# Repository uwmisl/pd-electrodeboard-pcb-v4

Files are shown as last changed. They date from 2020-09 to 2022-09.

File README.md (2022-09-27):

# Electrode Board v4

KiCad design for PurpleDrop electrode board with improved heater conductance, designed for 100x74mm film carrier and 50x50mm top plate.

This project is designed with KiCad v5.1.5.

## PDF Documentation

For a quick look, there is a [Schematic](PD_ElectrodeBoard_v4/outputs/PD_ElectrodeBoard_v4.1_sch.pdf) and [PCB fab drawing](PD_ElectrodeBoard_v4/outputs/PD_ElectrodeBoard_v4.1_fab.pdf)

## Project structure

Much of the board design is auto-generated by python scripts.

`FootprintGenerator.ipynb` generates the electrode and reservoir footprints.
They are all designed such that their origin should fall on the center of the
electrode "grid" positions. For this design, the pitch of the electrodes is
2.25mm. This script will generate a number of footprints, e.g. `electrode_points_1_40deg_rl.kicad_mod`.
The naming convention says that this footprint has 1 point per edge, the angle
of the points is 40 degrees, and it has points on the right and left edge (the
top and bottom are flat).

`FiducialFootprintGenerator.ipynb` generates a silkscreen footprint from an image file
(see `TagImages` directory), to put [april tags](https://github.com/AprilRobotics/apriltag)
onto the board as fidicuals for image processing. Each tag has a unique ID to aid in
identifying which tag (as well as which version of electrode board) has been
detected.

`LayoutGenerator.ipynb` generates a layout.yaml file for this
[kicad component layout plugin](https://github.com/mcbridejc/kicad_component_layout/).
This positions the electrodes, and selects between the different edge variants (e.g. trbl, tr)
based on neighboring electrodes in the grid.

This makes the process of experimenting with different electrode footprints and
layouts easier. Once the electrodes are positioned, the routing to the connectors
is done manually.

## BOM

| Part Number | Mfg | RefDes | Description | Qty |
| ----------- | --- | ------ | ----------- | --- |
| CLP-132-02-F-D-A  | Samtec | J1,J2  | 64-pin connectors      | 2   |
| 4929 | Keystone | H1-4 | #2-56 solderable threaded insert | 4 |
| PWR163S-25-25R0FE | Bourns | R1-4 | 25W resistor for heating | 4 |
| ZNI1000TA | Diodes Inc. | T1-4 | 1kohm RTD temperature sensor | 4 |
| S5B-PH-SM4-TB | JST | J3 | 5-pin connector for heaters | 1 |
| S8B-PH-SM4-TB | JST | J4 | 8-pin connector for RTDs | 1 |

## Revision History

### Version 4.1

- Shrinks width to fit reservoirs entirely under 50mmx50mm plate
- Corrects heater footprints
- Adds 2 internal layers to allow heaters to be located closer to the electrodes and
to provide additional thermal paths between them
- Flips connector pin labeling to match purpledrop
- 0.062" thick: 0.032" was not rigid enough
- Increases size of fiducials to 6mm and uses a unique value for each fiducial

### Version 4.0

Initial version

Issues:
- Undersized heating resistor footprints
- Mislabeled pin numbers (they do not match the purpledrop numbering)
- Fiducials were a bit too small; they silk screen resolution did not reproduce them well and sometimes they are difficult to detect

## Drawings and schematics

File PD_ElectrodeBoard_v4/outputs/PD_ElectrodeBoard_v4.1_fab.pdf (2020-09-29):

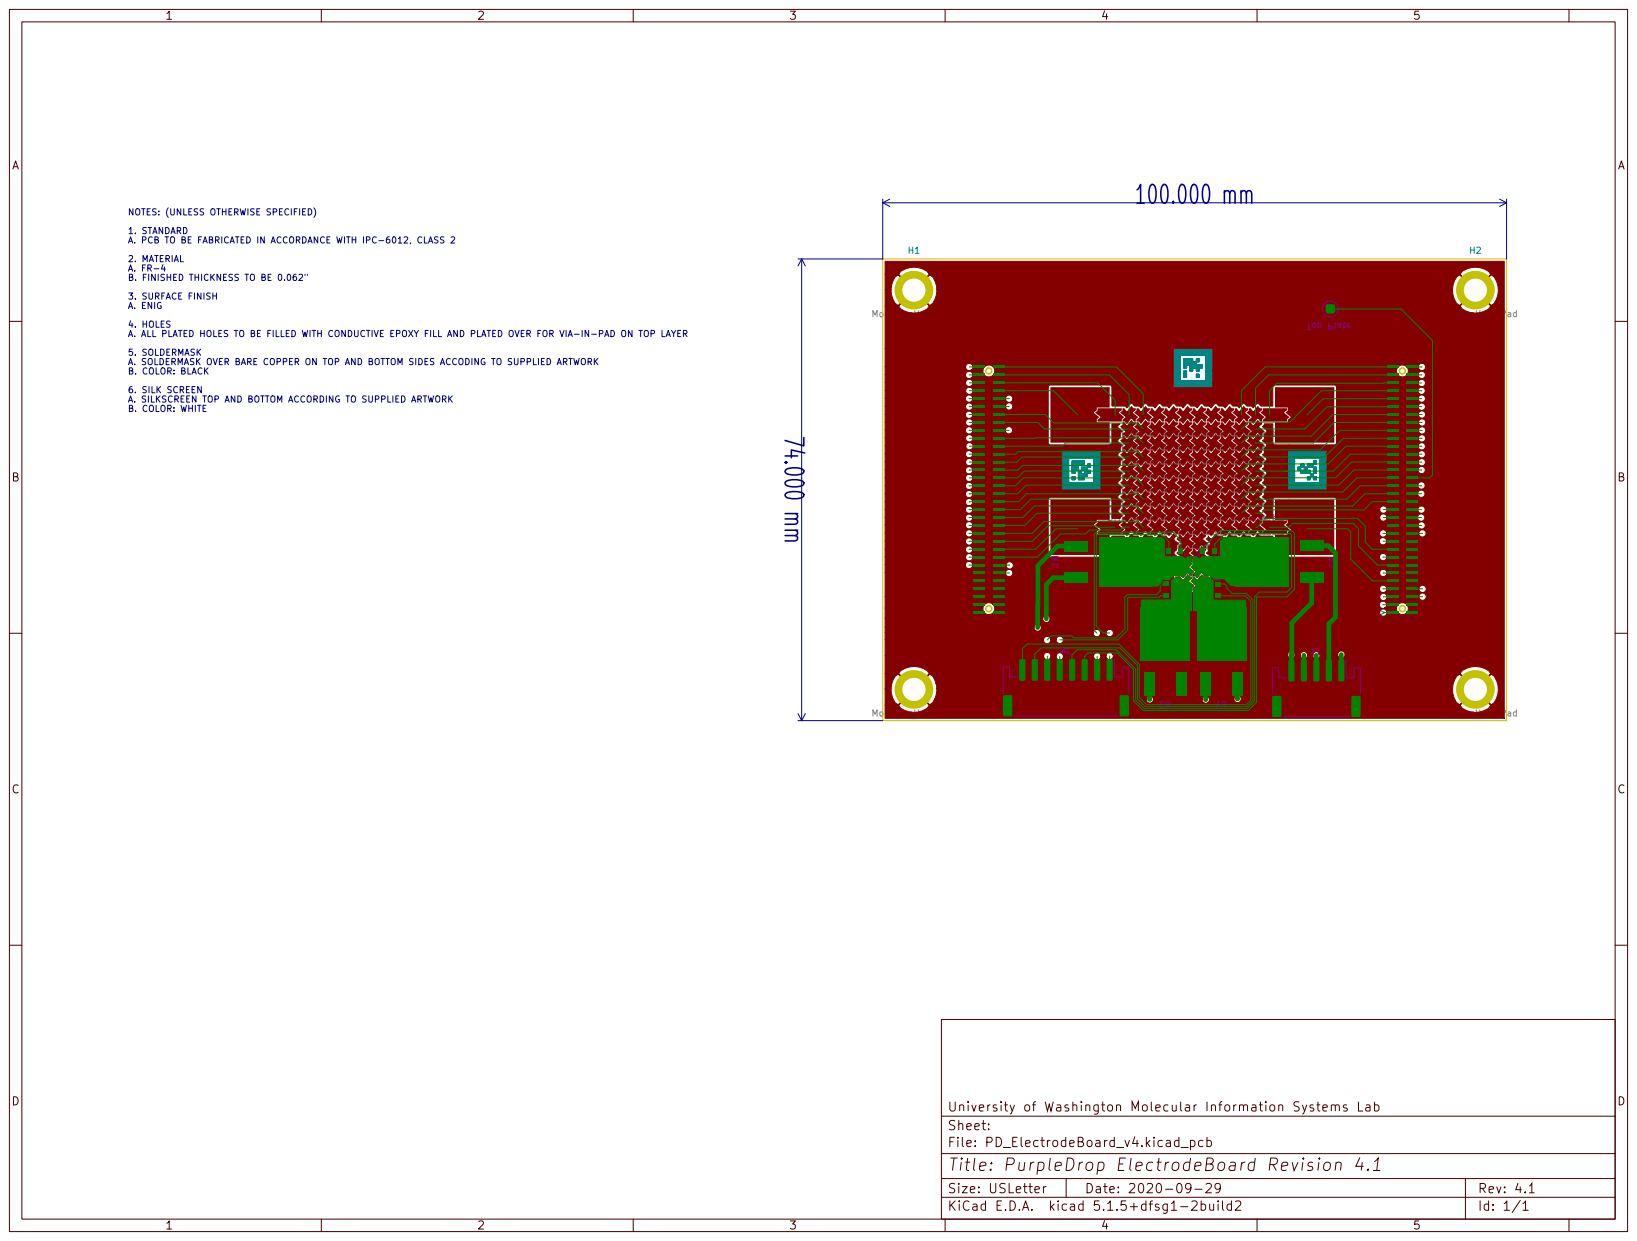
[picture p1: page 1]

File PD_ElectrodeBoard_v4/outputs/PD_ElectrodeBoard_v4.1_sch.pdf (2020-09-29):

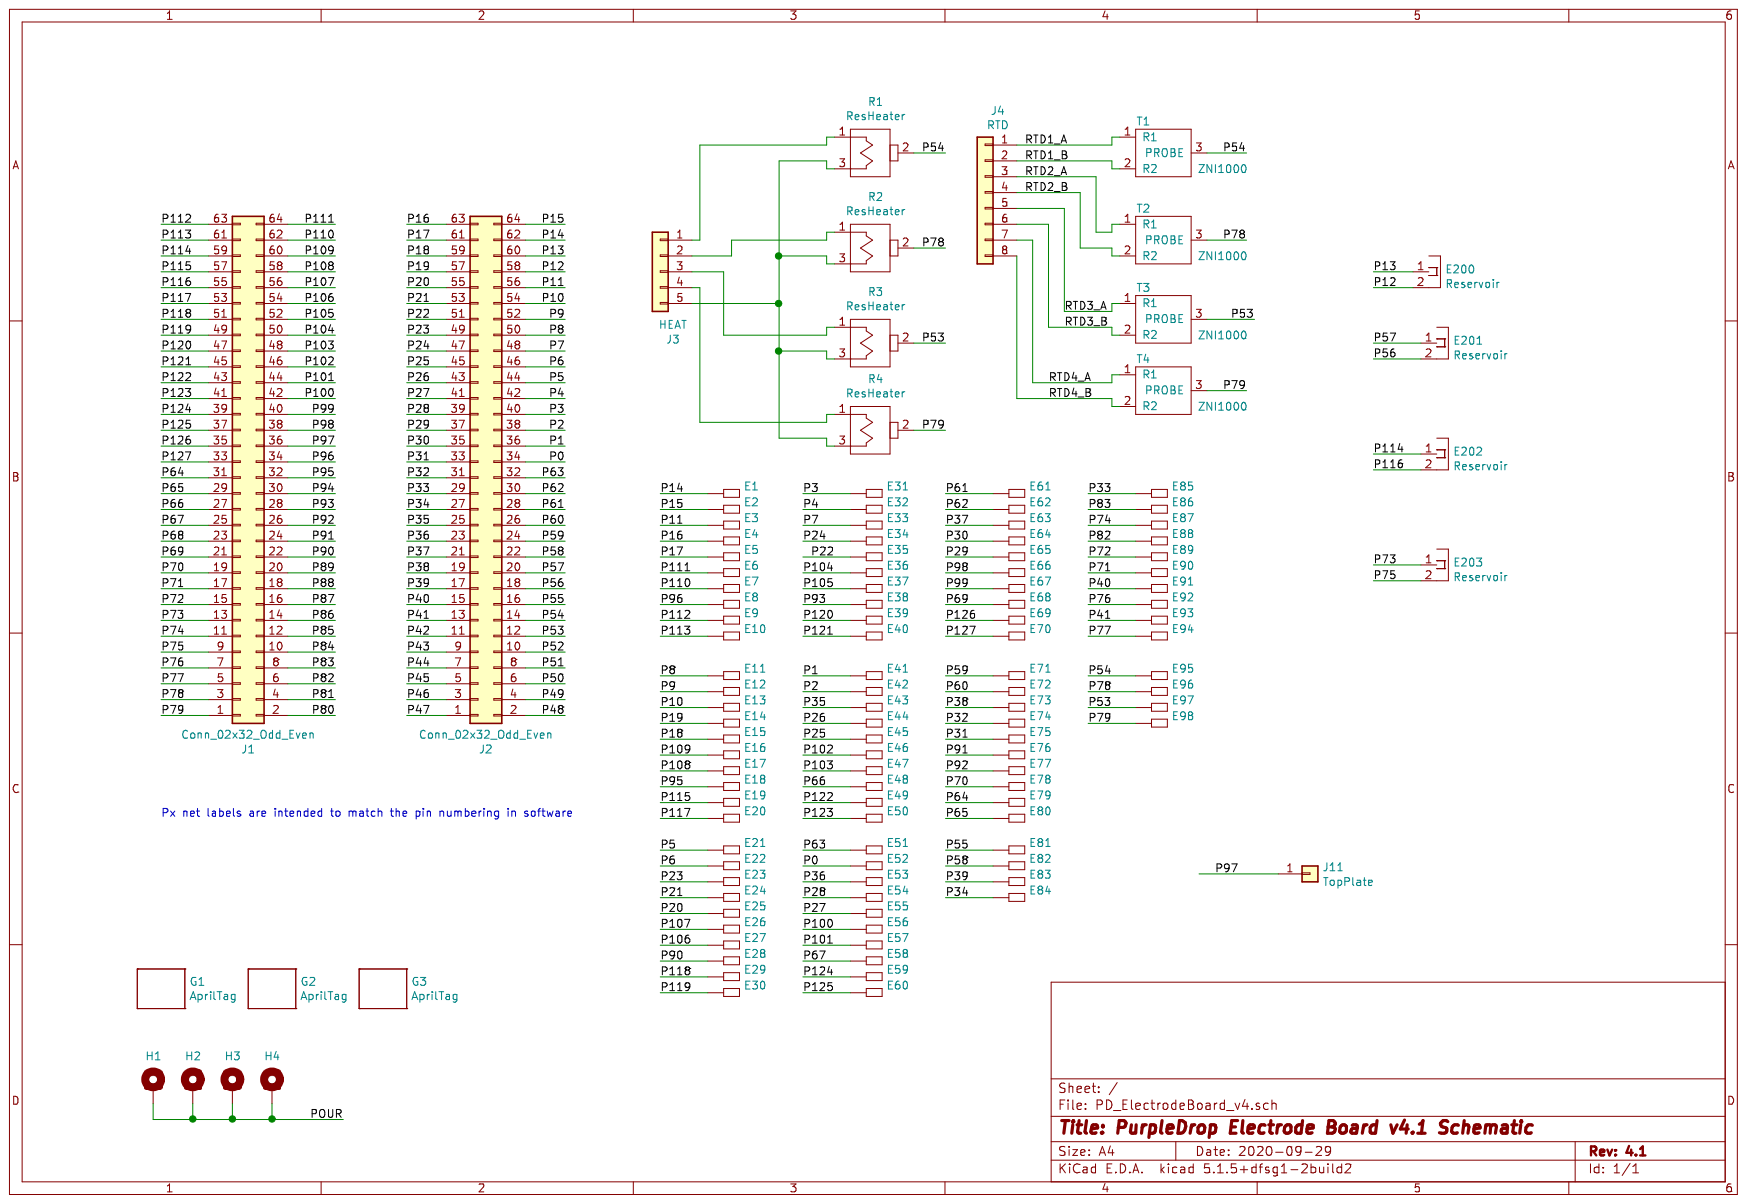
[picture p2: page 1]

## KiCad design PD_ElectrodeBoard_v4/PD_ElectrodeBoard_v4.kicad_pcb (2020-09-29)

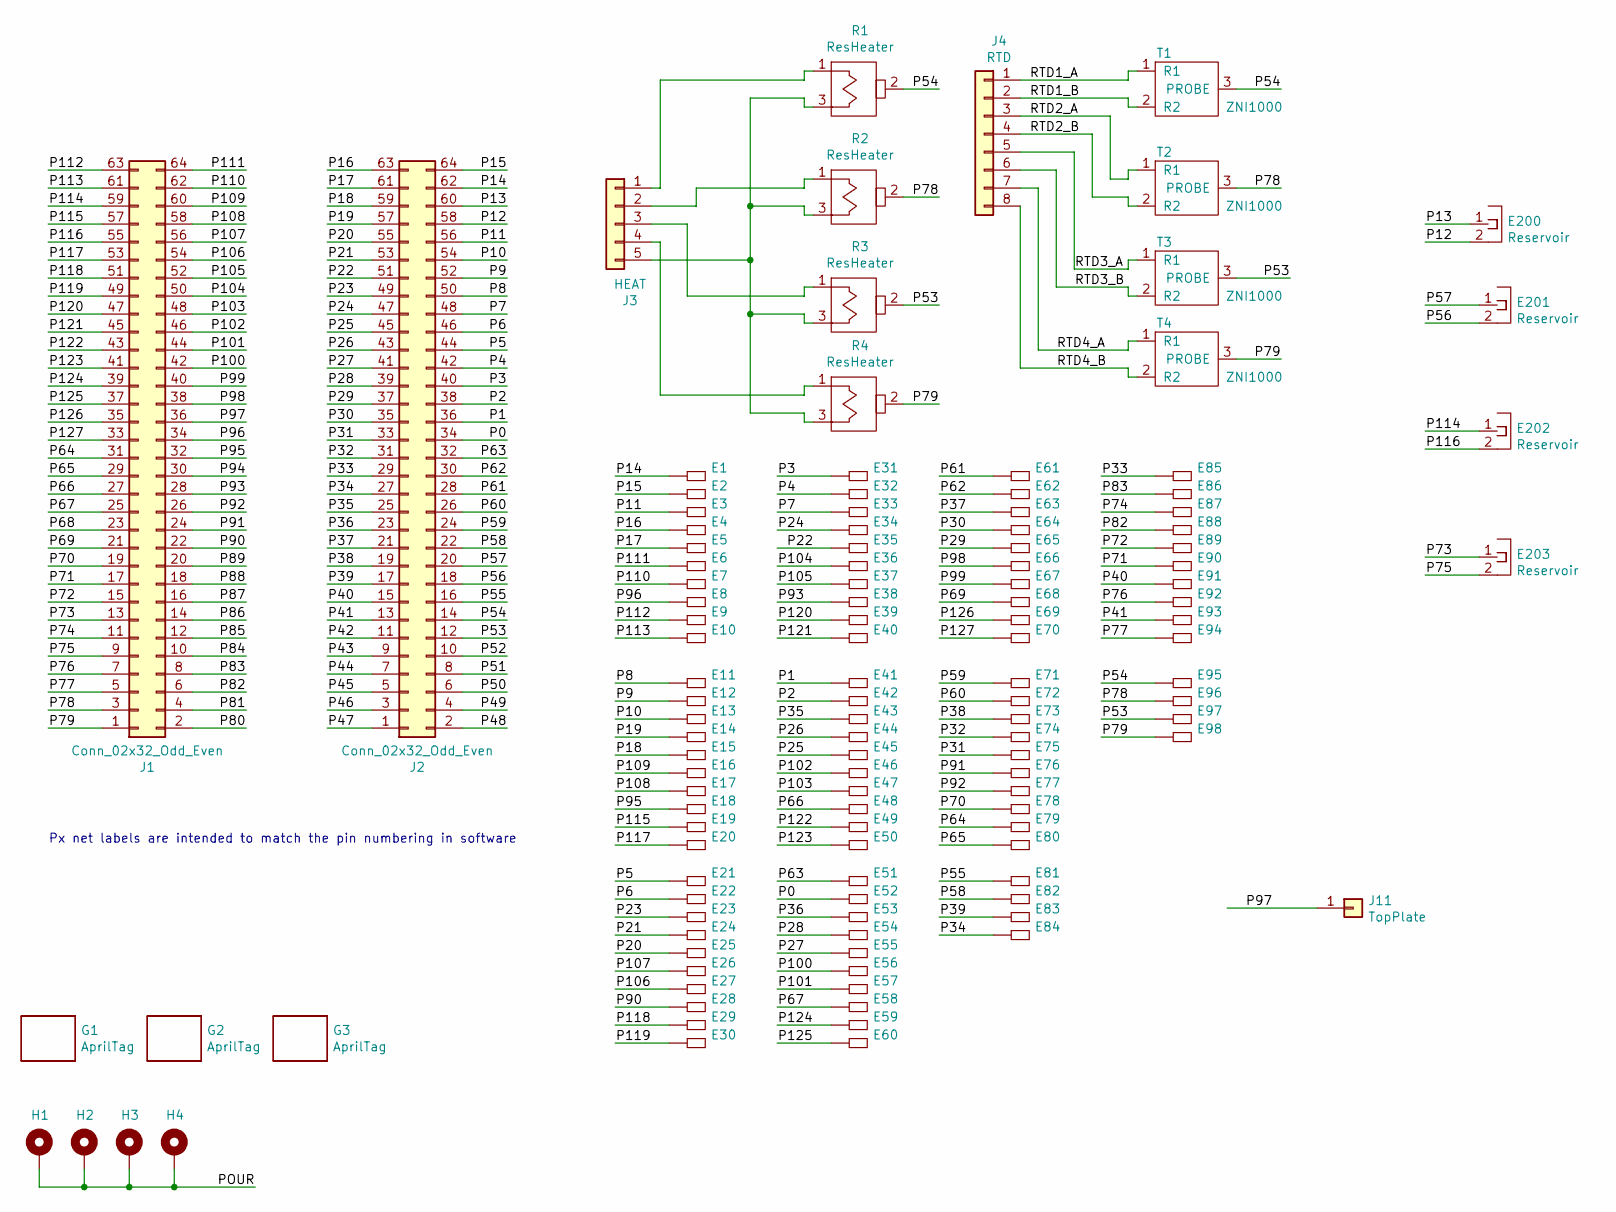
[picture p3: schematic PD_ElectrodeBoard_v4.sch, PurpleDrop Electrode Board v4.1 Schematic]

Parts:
E1, E2, E3, E4, E5, E6, E7, E8, E9, E10, E11, E12, E13, E14, E15, E16, E17, E18, E19, E20, E21, E22, E23, E24, E25, E26, E27, E28, E29, E30, E31, E32, E33, E34, E35, E36, E37, E38, E39, E40, E41, E42, E43, E44, E45, E46, E47, E48, E49, E50, E51, E52, E53, E54, E55, E56, E57, E58, E59, E60, E61, E62, E63, E64, E65, E66, E67, E68, E69, E70, E71, E72, E73, E74, E75, E76, E77, E78, E79, E80, E81, E82, E83, E84, E85, E86, E87, E88, E89, E90, E91, E92, E93, E94, E95, E96, E97, E98: DMFElectrode; electrode_points_1_40deg_trbl
E200, E201, E202, E203: Reservoir; reservoir_A_2.25mm
G1: AprilTag; tag36_11_00004_6.00mm
G2: AprilTag; tag36_11_00005_6.00mm
G3: AprilTag; tag36_11_00006_6.00mm
H1, H2, H3, H4: MountingHole_Pad; Keystone-4929
J1, J2: Conn_02x32_Odd_Even; CLP-132-02-F-D
J3: HEAT; JST_PH_S5B-PH-SM4-TB_1x05-1MP_P2.00mm_Horizontal
J4: RTD; JST_PH_S8B-PH-SM4-TB_1x08-1MP_P2.00mm_Horizontal
J11: TopPlate; TopPlatePad
R1, R2, R3, R4: ResHeater; PWR163_Resistor_DPAK
T1, T2, T3, T4: ZNI1000; SOT-23

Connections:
/P0: E52.1, J2.34
/P1: E41.1, J2.36
/P2: E42.1, J2.38
/P3: E31.1, J2.40
/P4: E32.1, J2.42
/P5: E21.1, J2.44
/P6: E22.1, J2.46
/P7: E33.1, J2.48
/P8: E11.1, J2.50
/P9: E12.1, J2.52
/P10: E13.1, J2.54
/P11: E3.1, J2.56
/P12: E200.2, J2.58
/P13: E200.1, J2.60
/P14: E1.1, J2.62
/P15: E2.1, J2.64
/P16: E4.1, J2.63
/P17: E5.1, J2.61
/P18: E15.1, J2.59
/P19: E14.1, J2.57
/P20: E25.1, J2.55
/P21: E24.1, J2.53
/P22: E35.1, J2.51
/P23: E23.1, J2.49
/P24: E34.1, J2.47
/P25: E45.1, J2.45
/P26: E44.1, J2.43
/P27: E55.1, J2.41
/P28: E54.1, J2.39
/P29: E65.1, J2.37
/P30: E64.1, J2.35
/P31: E75.1, J2.33
/P32: E74.1, J2.31
/P33: E85.1, J2.29
/P34: E84.1, J2.27
/P35: E43.1, J2.25
/P36: E53.1, J2.23
/P37: E63.1, J2.21
/P38: E73.1, J2.19
/P39: E83.1, J2.17
/P40: E91.1, J2.15
/P41: E93.1, J2.13
/P42: J2.11
/P43: J2.9
/P44: J2.7
/P45: J2.5
/P46: J2.3
/P47: J2.1
/P48: J2.2
/P49: J2.4
/P50: J2.6
/P51: J2.8
/P52: J2.10
/P53: E97.1, J2.12, R3.2 (TAB), T3.3 (PROBE)
/P54: E95.1, J2.14, R1.2 (TAB), T1.3 (PROBE)
/P55: E81.1, J2.16
/P56: E201.2, J2.18
/P57: E201.1, J2.20
/P58: E82.1, J2.22
/P59: E71.1, J2.24
/P60: E72.1, J2.26
/P61: E61.1, J2.28
/P62: E62.1, J2.30
/P63: E51.1, J2.32
/P64: E79.1, J1.31
/P65: E80.1, J1.29
/P66: E48.1, J1.27
/P67: E58.1, J1.25
/P68: J1.23
/P69: E68.1, J1.21
/P70: E78.1, J1.19
/P71: E90.1, J1.17
/P72: E89.1, J1.15
/P73: E203.1, J1.13
/P74: E87.1, J1.11
/P75: E203.2, J1.9
/P76: E92.1, J1.7
/P77: E94.1, J1.5
/P78: E96.1, J1.3, R2.2 (TAB), T2.3 (PROBE)
/P79: E98.1, J1.1, R4.2 (TAB), T4.3 (PROBE)
/P80: J1.2
/P81: J1.4
/P82: E88.1, J1.6
/P83: E86.1, J1.8
/P84: J1.10
/P85: J1.12
/P86: J1.14
/P87: J1.16
/P88: J1.18
/P89: J1.20
/P90: E28.1, J1.22
/P91: E76.1, J1.24
/P92: E77.1, J1.26
/P93: E38.1, J1.28
/P94: J1.30
/P95: E18.1, J1.32
/P96: E8.1, J1.34
/P97: J1.36, J11.1
/P98: E66.1, J1.38
/P99: E67.1, J1.40
/P100: E56.1, J1.42
/P101: E57.1, J1.44
/P102: E46.1, J1.46
/P103: E47.1, J1.48
/P104: E36.1, J1.50
/P105: E37.1, J1.52
/P106: E27.1, J1.54
/P107: E26.1, J1.56
/P108: E17.1, J1.58
/P109: E16.1, J1.60
/P110: E7.1, J1.62
/P111: E6.1, J1.64
/P112: E9.1, J1.63
/P113: E10.1, J1.61
/P114: E202.1, J1.59
/P115: E19.1, J1.57
/P116: E202.2, J1.55
/P117: E20.1, J1.53
/P118: E29.1, J1.51
/P119: E30.1, J1.49
/P120: E39.1, J1.47
/P121: E40.1, J1.45
/P122: E49.1, J1.43
/P123: E50.1, J1.41
/P124: E59.1, J1.39
/P125: E60.1, J1.37
/P126: E69.1, J1.35
/P127: E70.1, J1.33
/POUR: H1.1, H2.1, H3.1, H4.1
/RTD1_A: J4.1, T1.1 (R1)
/RTD1_B: J4.2, T1.2 (R2)
/RTD2_A: J4.3, T2.1 (R1)
/RTD2_B: J4.4, T2.2 (R2)
/RTD3_A: J4.5, T3.1 (R1)
/RTD3_B: J4.6, T3.2 (R2)
/RTD4_A: J4.7, T4.1 (R1)
/RTD4_B: J4.8, T4.2 (R2)
unnamed: J3.1, R1.1
unnamed: J3.2, R2.1
unnamed: J3.3, R3.1
unnamed: J3.4, R4.1
unnamed: J3.5, R1.3, R2.3, R3.3, R4.3

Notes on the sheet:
Px net labels are intended to match the pin numbering in software

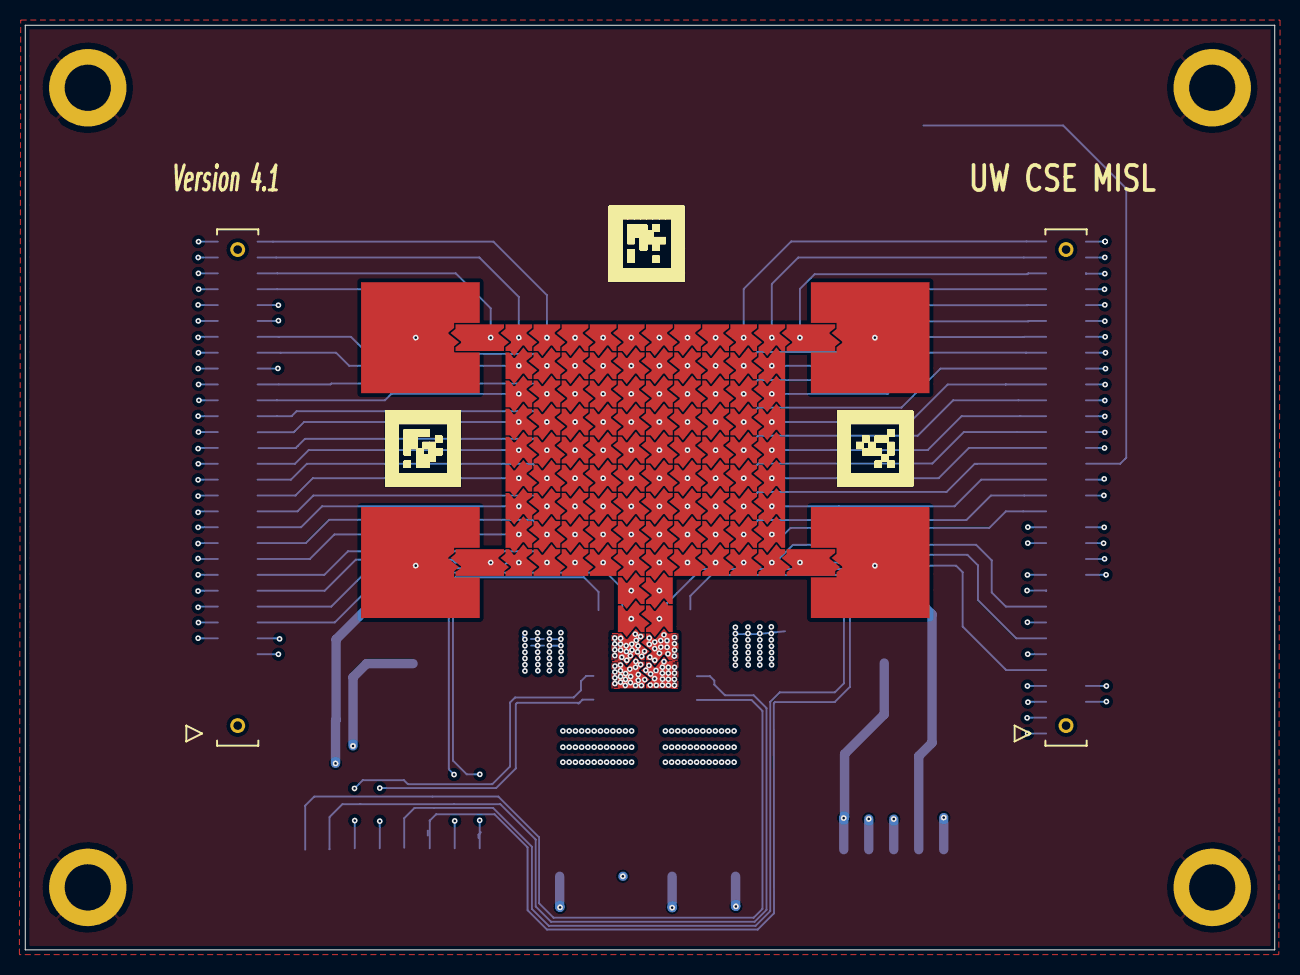
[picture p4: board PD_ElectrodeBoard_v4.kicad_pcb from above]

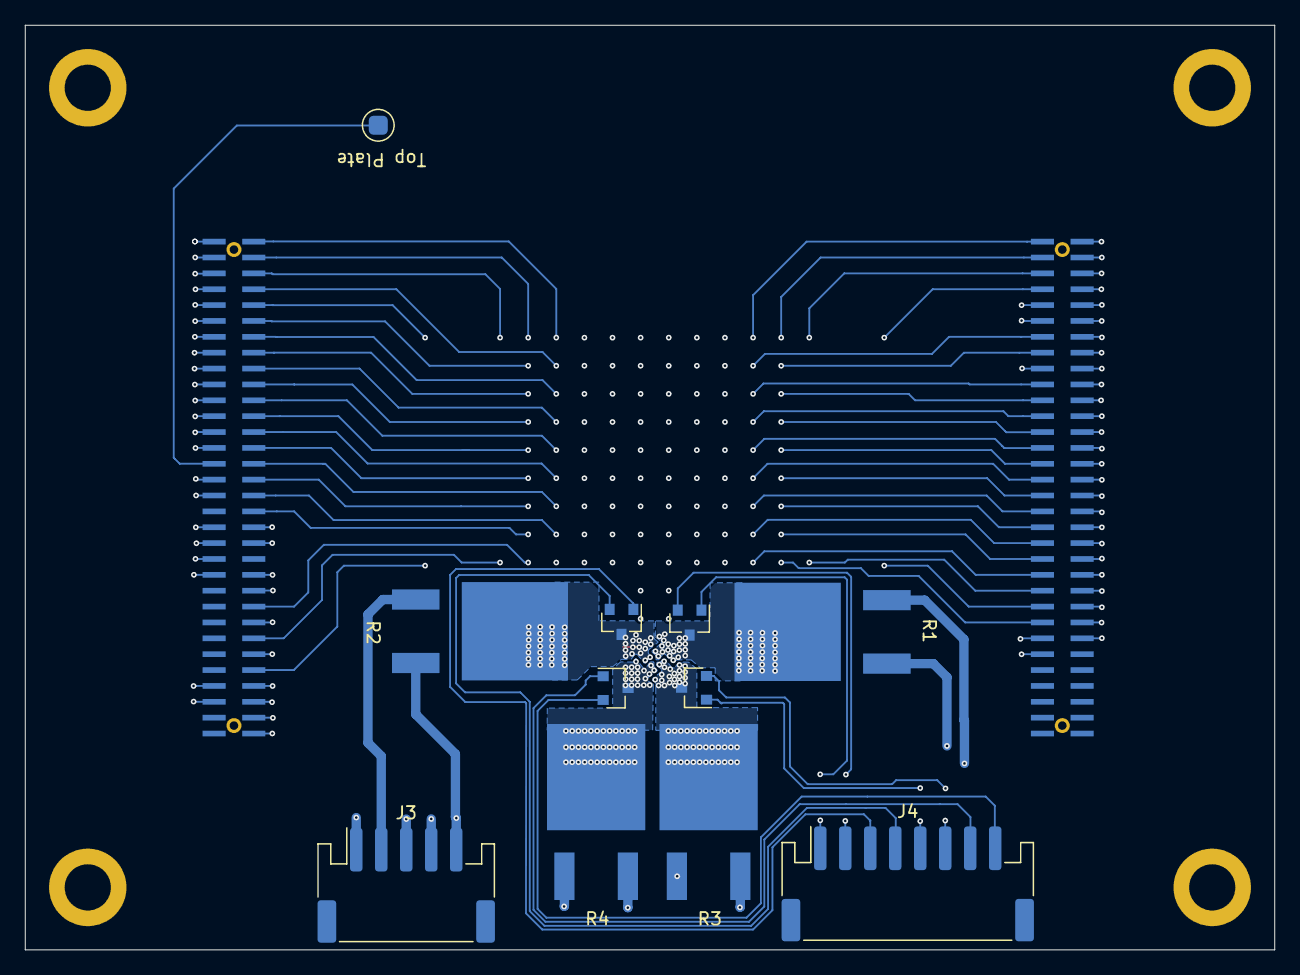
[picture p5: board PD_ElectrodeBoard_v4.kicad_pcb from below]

Board: 4 copper layers, 100.0 x 74.0 mm, 122 parts (11 on the bottom side), 121 nets.

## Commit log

2020-03-06 Add finished electrode board
    [PD_ElectrodeBoard_v4-B_Cu.gbr, PD_ElectrodeBoard_v4-B_Mask.gbr, PD_ElectrodeBoard_v4-Cmts_User.gbr, PD_ElectrodeBoard_v4-Edge_Cuts.gbr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]
2020-03-06 Add spacer project
    [spacer-B_Cu.gbr, spacer-B_Mask.gbr, spacer-Edge_Cuts.gbr, spacer-F_Cu.gbr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]
2020-03-10 Add step file
    [PD_ElectrodeBoard_v4.step]
2020-03-10 Re-export gerbers with drill files
    [PD_ElectrodeBoard_v4-B_Cu.gbr, PD_ElectrodeBoard_v4-B_Mask.gbr, PD_ElectrodeBoard_v4-Cmts_User.gbr, PD_ElectrodeBoard_v4-Edge_Cuts.gbr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]
2020-09-29 new revision 4.1 of electrode board
    [PD_ElectrodeBoard_v4-B_Cu.gbr, PD_ElectrodeBoard_v4-B_Mask.gbr, PD_ElectrodeBoard_v4-B_Paste.gbr, PD_ElectrodeBoard_v4-B_SilkS.gbr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]

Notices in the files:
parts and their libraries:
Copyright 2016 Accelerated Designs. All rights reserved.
